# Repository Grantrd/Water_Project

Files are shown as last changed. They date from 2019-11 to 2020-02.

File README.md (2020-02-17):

# Water Quality Monitoring Project
This project for Dr. Gary Mahoney and Dr. Wei Wu, a collaboration between Scott Heggen, Wei Wu and Rodney Grant. It is meant to allow for the measuring and recording of the quality of water in lakes. The project consists of code written in the Arduino ide, using many of its common libraries. It utulizes Eagle Autocad Software for making the schematics and boards, and _________ to mill the PCB's. This is a school project funded by Berea College.

## Specifications
The board we are creating is made for an Arduino Pro Mini, and acts as a shield for it. Therefore the legs of the Pro will need to be soldered going up and have the board sit on top of the Arduino. The board is 1.04 inches across by 1.79 inches long. 

## Required Components
To use this project you will need: 
- An Arduino Pro Mini
- To be able to mill a PCB/ have the milled PCB 
- A 4.7K ohm resistor and a Digital Temperature probe
- An Arduino Micro SD adapter.  
- An analog light sensor
- A real time clock
- 2 1K to 500K Potentiometers
- A set of molex connectors
- A 6 Pin 90 degree Female header terminal.   

## Getting Started
To use the project you need to install the Arduino programming software. Open the code folder of the project, and copy the contents of the arduino libraries folder into the libraries folder of your arduino software, typically located in yourUserName\Documents\Arduino\libraries. Plug in your Arduino Mini Pro and open the Arduino Software. In the software go to "tools" -- "board" -- "Arduino Pro or Pro Mini". Then Go to open and select the Gary_Node_Temp.ino file located in the Arduino Code folder inside the Code folder of the Project. Then Go to "tools" -- "port" and select the port with the arduino connected, you can unplug and replug the arduino to see which port it connects to. Finally verify and upload the code onto the arduino. If the code will not verify, make sure the libraries are located in the correct folder.  

## The Board
Note if you already have the PCB, you can skip the milling section.  

### Milling the Board
...

### Soldering the board 
To solder the board you will need a soldering iron, solder, a milled PCB, and all of the required components listed above. 
You will need to solder the components for the board according to their location on the color coded diagram found under Board Layout. 

For the following components you will need to solder female ended molexes connectors to the board in place of the components, and solder male headed molex connectors to the ends of the components. They will then plug into each other.
- Temperature Probe
- Real Time Clock
- Power Switch
- Light Sensor

For the following components you will need to solder the components themselves to the board directly.
- Power Switch
- 4.7K Resistor
- 2 Potentiometers

For the Micro SD Writer you need to solder a 90 degree 6 pin female header terminal.

### Board Layout
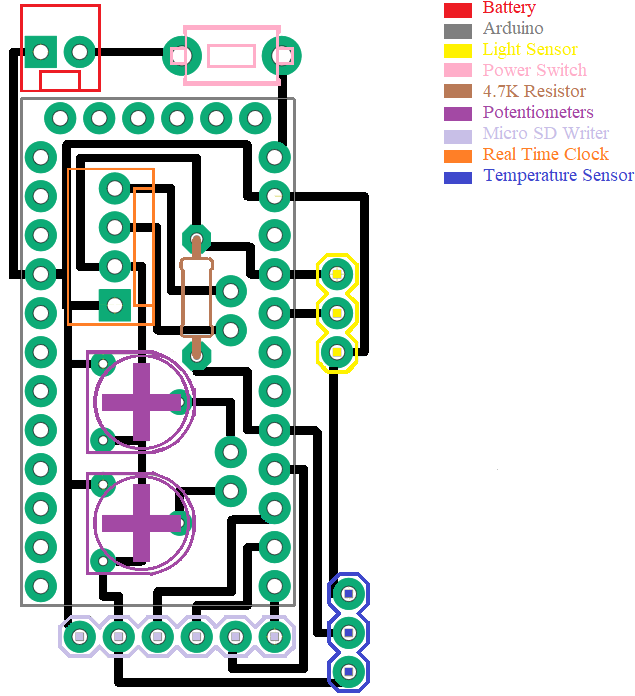
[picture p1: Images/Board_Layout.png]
Board Layout Board


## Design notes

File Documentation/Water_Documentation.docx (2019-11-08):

Water Project Documentation

Parts List/ To Buy

The Arduino we are using, we need 4: https://www.amazon.com/ARCELI-Digispark-Development-Kickstarter-ATTiny167/dp/B07KBFNXMC/ref=sr_1_1?keywords=digispark+pro&qid=1571411723&sr=8-1

The light sensor we need 15:

https://www.adafruit.com/product/1384

The temperature Probe we need one pack of 5:

https://www.amazon.com/Vktech-Waterproof-Digital-Temperature-DS18b20/dp/B00EU70ZL8/ref=sr_1_3?keywords=DS18B20&qid=1571412670&sr=8-3

The Molex connectors:

https://www.amazon.com/Hilitchi-Housing-Connector-Adapter-Perfectly-Compatible/dp/B015Y6JOUG/ref=sr_1_10?keywords=molex&qid=1571412741&sr=8-10

Vertical sliding Switch:

https://www.amazon.com/LIYUDL-Position-Vertical-Switch-SS12D00G3/dp/B075TYP6C5/ref=sr_1_26?hvadid=12092202914&hvbmt=be&hvdev=c&hvqmt=e&keywords=vertical+slide+switch&qid=1572214992&sr=8-26#customerReviews

Schematic/Parts Pinout,

1. Battery connector
2. Temperature probe -pinout: https://external-content.duckduckgo.com/iu/?u=https%3A%2F%2Ftse2.mm.bing.net%2Fth%3Fid%3DOIP.awUXVL5WOeqGfPSrxxb7ewAAAA%26pid%3DApi&f=1
3. Light sensor
4. Real Time clock - DS3231 - pinout: https://components101.com/modules/ds3231-rtc-module-pinout-circuit-datasheet
5. Micro SD Storage Expansion Board Mciro SD TF Card - pinout: https://www.instructables.com/id/Micro-SD-Card-Tutorial/
6. Arduino Tiny - pinout : http://digispark.s3.amazonaws.com/DigisparkProDiagram2.png
7. Power switch - Pinout: https://www.amazon.com/microtivity-IM231-3-pin-Slide-Switch/dp/B008CZIFQG/ref=sr_1_2?keywords=Vertical+Slide+Switch&qid=1572024991&s=electronics&sr=1-2

Board Layout/ Pinout:

1. Temp sensor pinout: PA7 (D5)
2. Light sensor pinout: PA3 (A9)
3. Micro SD pinout: (SC - PB3 (D4), (Mosi - PA4 (Mosi), (Miso - (PA2 (Miso)), (SCK- PA5(SCK)))
4. RT Clock - pinout: ((SDA - PB0 (SDA)), (SCL PB2 (SCL)))

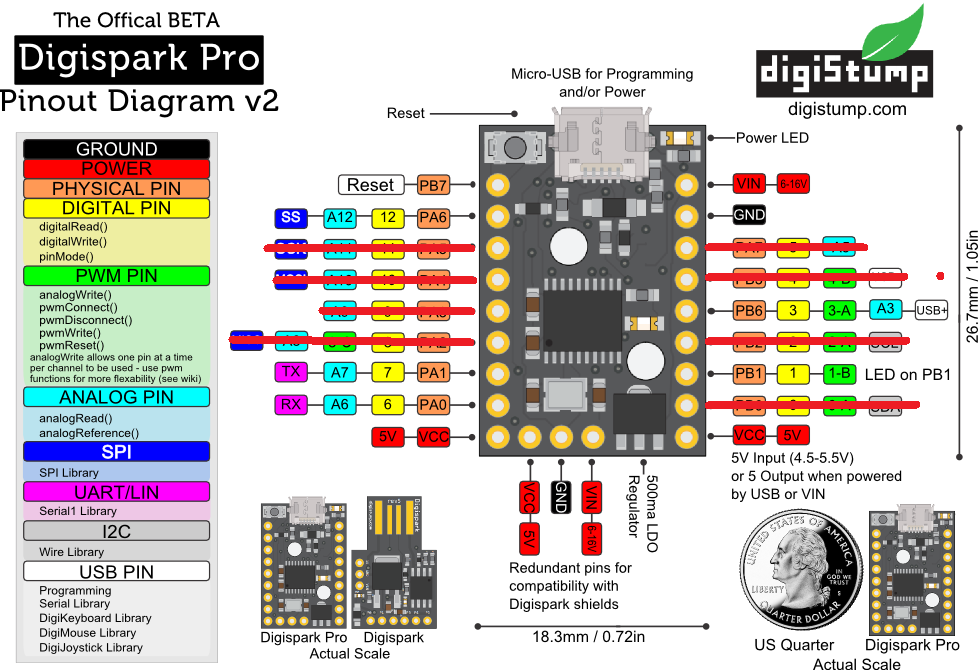
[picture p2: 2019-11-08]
resources/images/DigisparkPInout in progress.png

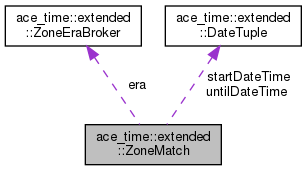
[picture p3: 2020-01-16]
code/Arduino Libraries/AceTime/docs/html/structace__time_1_1extended_1_1ZoneMatch__coll__graph.png

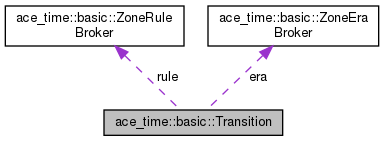
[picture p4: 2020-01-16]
code/Arduino Libraries/AceTime/docs/html/structace__time_1_1basic_1_1Transition__coll__graph.png

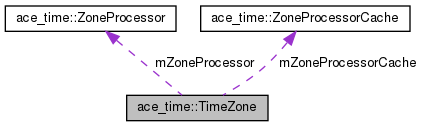
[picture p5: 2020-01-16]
code/Arduino Libraries/AceTime/docs/html/classace__time_1_1TimeZone__coll__graph.png

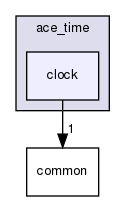
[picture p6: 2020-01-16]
code/Arduino Libraries/AceTime/docs/html/dir_1a3db1509c5a81eeb8e8fbfe5ac0febc_dep.png

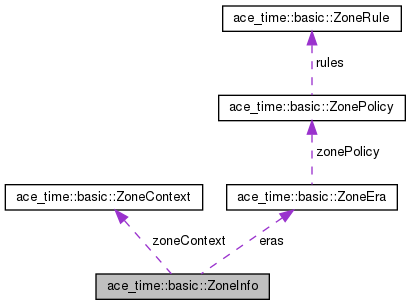
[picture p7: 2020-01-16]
code/Arduino Libraries/AceTime/docs/html/structace__time_1_1basic_1_1ZoneInfo__coll__graph.png

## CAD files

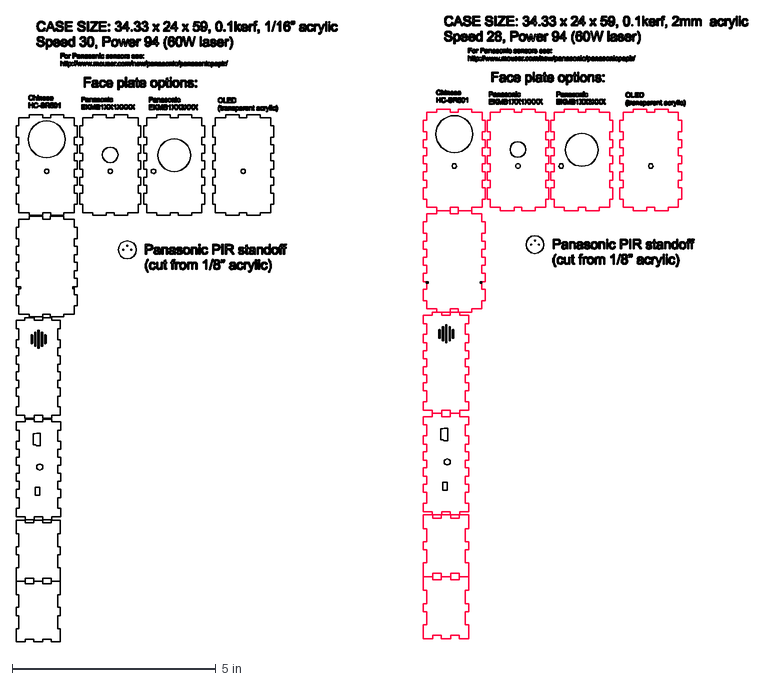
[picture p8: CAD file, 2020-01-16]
code/Arduino Libraries/RFM69_LowPowerLab/Examples/MotionMote/LasercutCase_R3.dxf
18.0 x 15.4 in

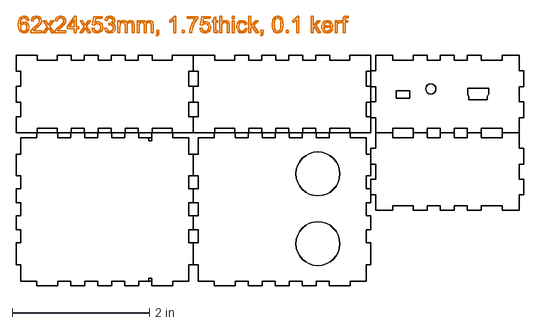
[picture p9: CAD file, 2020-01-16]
code/Arduino Libraries/RFM69_LowPowerLab/Examples/SonarMote/SonarMote_lasercut plans_1.75mm acrylic.dxf
7.41 x 3.94 in

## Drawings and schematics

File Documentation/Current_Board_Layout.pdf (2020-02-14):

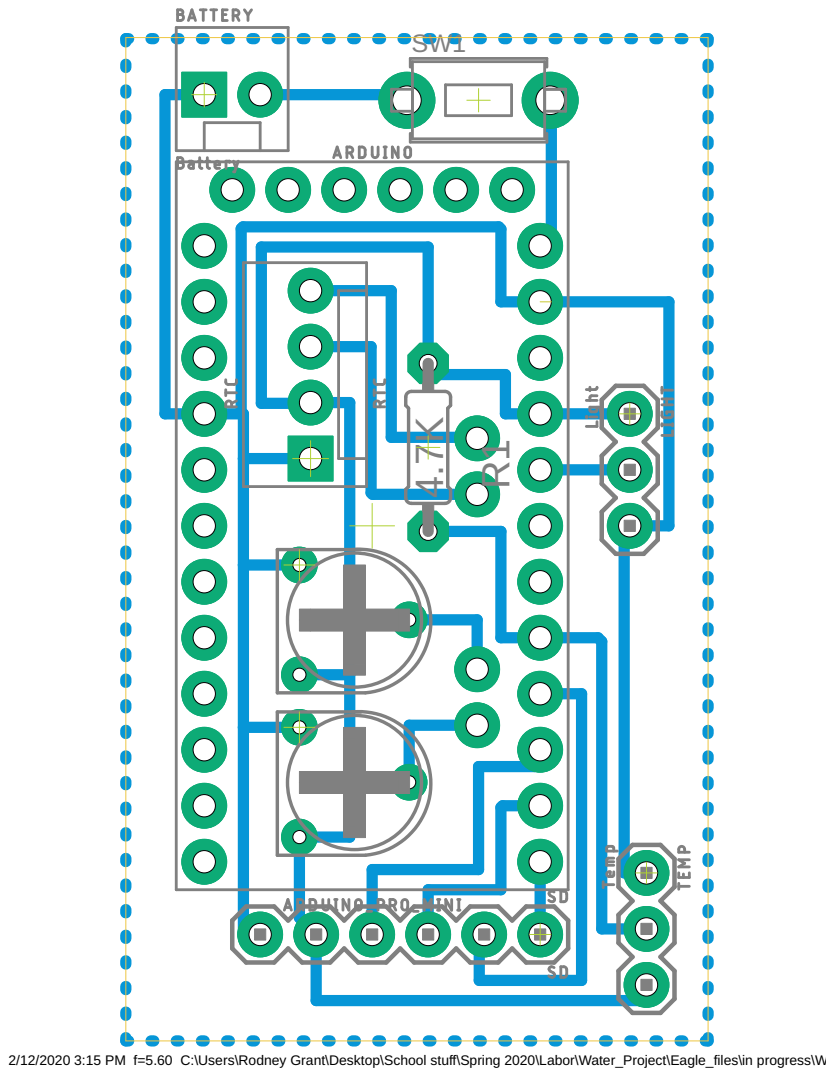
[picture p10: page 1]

2/12/2020 3:15 PM f=5.60 C:\Users\Rodney Grant\Desktop\School stuff\Spring 2020\Labor\Water_Project\Eagle_files\in progress\Water_Schematic2_1.brd

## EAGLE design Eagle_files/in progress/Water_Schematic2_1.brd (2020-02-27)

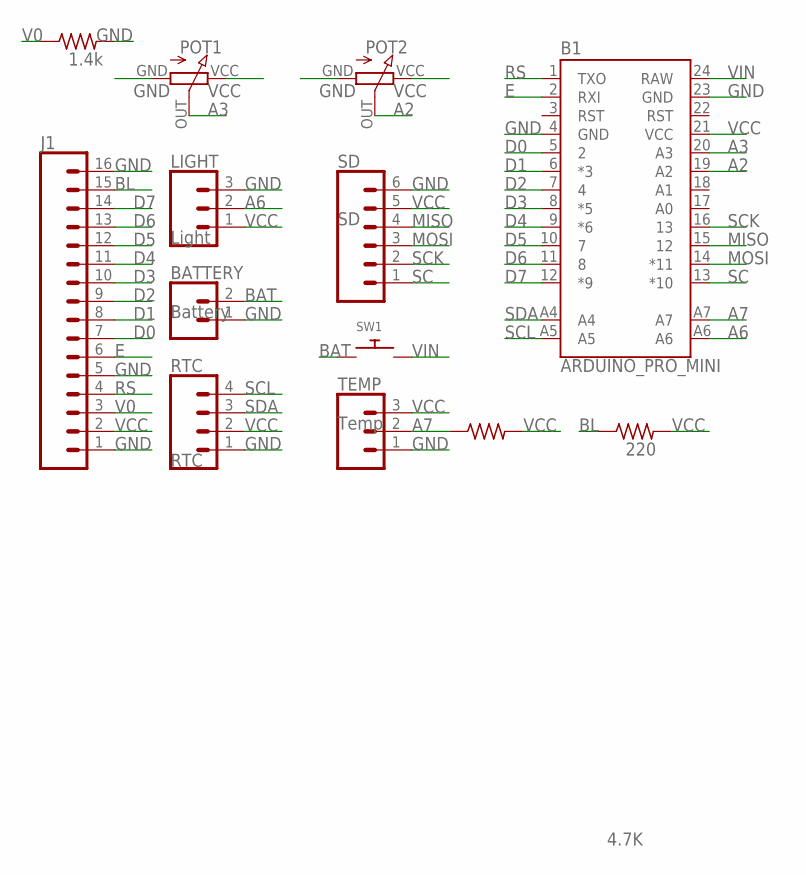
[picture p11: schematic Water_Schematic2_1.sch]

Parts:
B1: ARDUINO_PRO_MINI
BATTERY: Battery; MOLEX-1X2
J1: CONN_16; 1X16
LIGHT: Light; 1X03
POT1, POT2: RM_065
R1: 4.7K; 0204/7
R2: 220; 0204/7
R3: 1.4k; 0204/7
RTC: RTC; MOLEX-1X4
SD: SD; 1X06
SW1: SWITCH_PUSHBUTTONEVQ-PE; TACT_PANA-EVQ
TEMP: Temp; 1X03

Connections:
A2: B1.19 (A2), POT2.OUT
A3: B1.20 (A3), POT1.OUT
A6: B1.A6, LIGHT.2
A7: B1.A7, R1.1, TEMP.2
BAT: BATTERY.2, SW1.P$1
BL: J1.15, R2.1
D0: B1.5 (2), J1.7
D1: B1.6 (*3), J1.8
D2: B1.7 (4), J1.9
D3: B1.8 (*5), J1.10
D4: B1.9 (*6), J1.11
D5: B1.10 (7), J1.12
D6: B1.11 (8), J1.13
D7: B1.12 (*9), J1.14
E: B1.2 (RXI), J1.6
GND: B1.4 (GND), B1.23 (GND), BATTERY.1, J1.1, J1.5, J1.16, LIGHT.3, POT1.GND (GROUND), POT2.GND (GROUND), R3.2, RTC.1, SD.6, TEMP.1
MISO: B1.15 (12), SD.4
MOSI: B1.14 (*11), SD.3
RS: B1.1 (TXO), J1.4
SC: B1.13 (*10), SD.1
SCK: B1.16 (13), SD.2
SCL: B1.A5, RTC.4
SDA: B1.A4, RTC.3
V0: J1.3, R3.1
VCC: B1.21 (VCC), J1.2, LIGHT.1, POT1.VCC, POT2.VCC, R1.2, R2.2, RTC.2, SD.5, TEMP.3
VIN: B1.24 (RAW), SW1.P$2

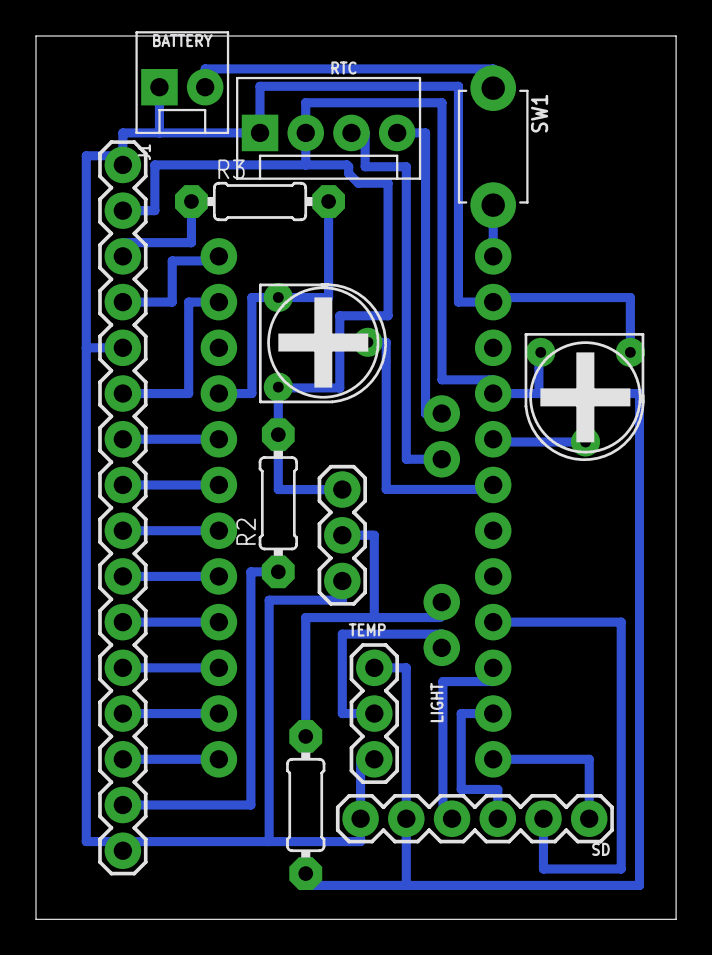
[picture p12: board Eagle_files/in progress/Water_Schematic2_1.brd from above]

Board: 2 copper layers, 35.6 x 49.1 mm, 13 parts (0 on the bottom side), 26 nets.

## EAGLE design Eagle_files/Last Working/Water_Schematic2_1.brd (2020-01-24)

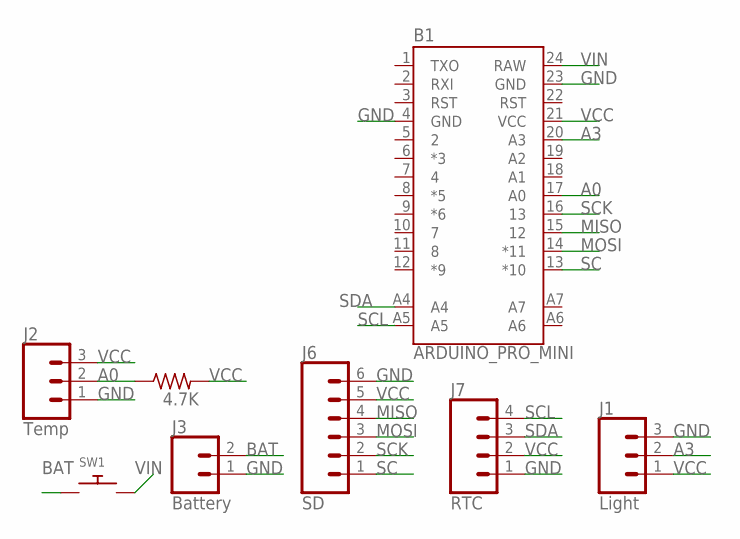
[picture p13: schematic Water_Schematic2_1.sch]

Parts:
B1: ARDUINO_PRO_MINI
J1: Light; 1X03
J2: Temp; 1X03
J3: Battery; MOLEX-1X2
J6: SD; 1X06
J7: RTC; MOLEX-1X4
R1: 4.7K; 0204/7
SW1: SWITCH_PUSHBUTTONEVQ-PE; TACT_PANA-EVQ

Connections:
A0: B1.17 (A0), J2.2, R1.1
A3: B1.20 (A3), J1.2
BAT: J3.2, SW1.P$1
GND: B1.4 (GND), B1.23 (GND), J1.3, J2.1, J3.1, J6.6, J7.1
MISO: B1.15 (12), J6.4
MOSI: B1.14 (*11), J6.3
SC: B1.13 (*10), J6.1
SCK: B1.16 (13), J6.2
SCL: B1.A5, J7.4
SDA: B1.A4, J7.3
VCC: B1.21 (VCC), J1.1, J2.3, J6.5, J7.2, R1.2
VIN: B1.24 (RAW), SW1.P$2

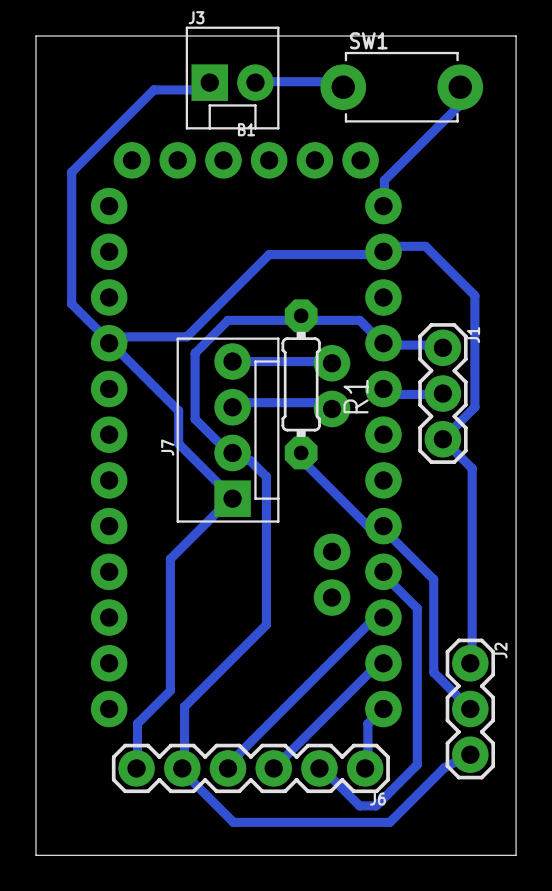
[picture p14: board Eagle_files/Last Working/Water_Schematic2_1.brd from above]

Board: 2 copper layers, 26.7 x 45.5 mm, 8 parts (0 on the bottom side), 12 nets.

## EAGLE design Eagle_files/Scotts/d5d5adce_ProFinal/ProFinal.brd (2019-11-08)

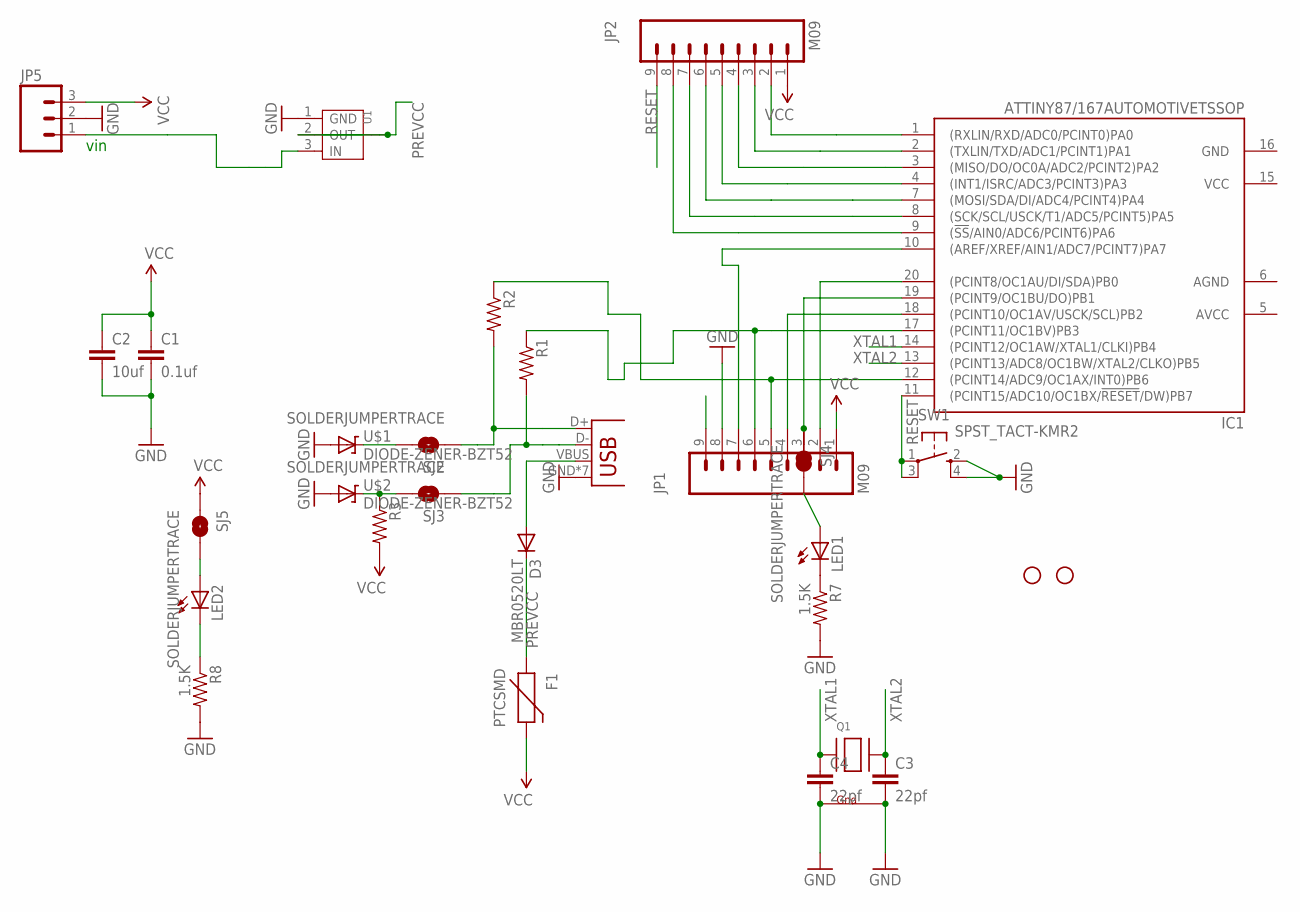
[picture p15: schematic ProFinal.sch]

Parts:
C1: 0.1uf; 0603-CAP
C2: 10uf; 0805
C3, C4: 22pf; 0603-CAP
D3: MBR0520LT; SOD123
F1: PTCSMD; PTC-1206
IC1: ATTINY87/167AUTOMOTIVETSSOP; TSSOP20
JP1, JP2: M09; 1X09
JP5: M03PTH; 1X03
LED1, LED2: LEDCHIP-LED0805; CHIP-LED0805
Q1: XTAL-4-3225; NX3225
R1, R2, R3: RESISTOR0603-RES; 0603-RES
R7, R8: 1.5K; 0603-RES
SJ2, SJ3, SJ4, SJ5: SOLDERJUMPERTRACE; SJ_2S-TRACE
STANDOFF3, STANDOFF4: STAND-OFFTIGHT; STAND-OFF-TIGHT
SW1: SPST_TACT-KMR2; KMR2
U1: LD1117SOT89; SOT89
U$1, U$2: DIODE-ZENER-BZT52; SOD-323
X1: USB-MICROB

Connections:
GND: C1.2, C2.2, C3.2, C4.2, IC1.16 (GND), JP1.8, JP5.2, Q1.2 (G2), Q1.4 (G1), R7.2, R8.2, SW1.2 (S), SW1.4 (S1), U1.1 (GND), U$1.2 (A), U$2.2 (A), X1.GND, X1.P1 (GND), X1.P2 (GND), X1.P3 (GND), X1.P4 (GND), X1.P5 (GND), X1.P6 (GND)
unnamed: IC1.20 ((PCINT8/OC1AU/DI/SDA)PB0), JP1.2
unnamed: IC1.12 ((PCINT14/ADC9/OC1AX/INT0)PB6), JP1.5, R2.1
unnamed: IC1.19 ((PCINT9/OC1BU/DO)PB1), JP1.3, SJ4.1
unnamed: IC1.1 ((RXLIN/RXD/ADC0/PCINT0)PA0), JP2.2
unnamed: IC1.2 ((TXLIN/TXD/ADC1/PCINT1)PA1), JP2.3
unnamed: IC1.3 ((MISO/DO/OC0A/ADC2/PCINT2)PA2), JP2.4
unnamed: IC1.4 ((INT1/ISRC/ADC3/PCINT3)PA3), JP2.5
unnamed: IC1.7 ((MOSI/SDA/DI/ADC4/PCINT4)PA4), JP2.6
unnamed: IC1.18 ((PCINT10/OC1AV/USCK/SCL)PB2), JP1.4
unnamed: R1.2, SJ3.1, X1.D-
unnamed: R2.2, SJ2.1, X1.D+
unnamed: IC1.8 ((SCK/SCL/USCK/T1/ADC5/PCINT5)PA5), JP2.7
unnamed: IC1.9 ((!SS!/AIN0/ADC6/PCINT6)PA6), JP2.8
unnamed: IC1.10 ((AREF/XREF/AIN1/ADC7/PCINT7)PA7), JP1.7
unnamed: IC1.17 ((PCINT11/OC1BV)PB3), JP1.6, R1.1
unnamed: SJ2.2, U$1.1 (C)
unnamed: R3.1, SJ3.2, U$2.1 (C)
unnamed: LED1.C, R7.1
unnamed: LED1.A, SJ4.2
unnamed: LED2.A, SJ5.2
unnamed: LED2.C, R8.1
unnamed: D3.A, X1.VBUS
PREVCC: D3.C, F1.1, U1.2 (OUT), U1.4 (TAB)
RESET: IC1.11 ((PCINT15/ADC10/OC1BX/!RESET!/DW)PB7), JP2.9, SW1.1, SW1.3 (P1)
VCC: C1.1, C2.1, F1.2, IC1.15 (VCC), JP1.1, JP2.1, JP5.3, R3.2, SJ5.1
VIN: JP1.9, JP5.1, U1.3 (IN)
XTAL1: C4.1, IC1.14 ((PCINT12/OC1AW/XTAL1/CLKI)PB4), Q1.1 (X1)
XTAL2: C3.1, IC1.13 ((PCINT13/ADC8/OC1BW/XTAL2/CLKO)PB5), Q1.3 (X2)

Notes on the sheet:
vin

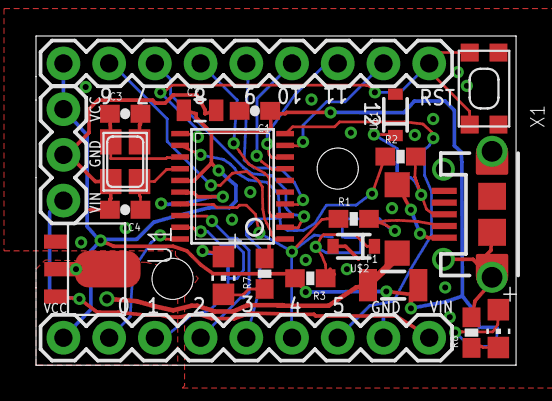
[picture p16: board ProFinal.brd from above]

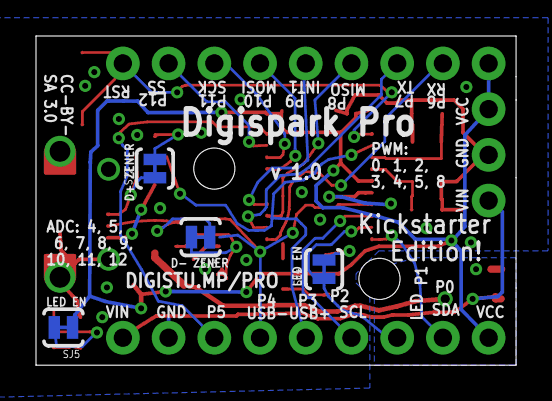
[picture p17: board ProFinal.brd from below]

Board: 2 copper layers, 26.7 x 18.3 mm, 29 parts (4 on the bottom side), 29 nets.

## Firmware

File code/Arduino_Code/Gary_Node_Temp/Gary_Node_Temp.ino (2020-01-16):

#include <OneWire.h>        //Temp (install from library manager)
#include <DallasTemperature.h>  //Temp (install from library manager)
#include <DS3231.h> //RTC  (install from library manager)
#include "SD.h"   //SD card (install from library manager)
#include "LowPower.h" // low power consumption (cpp and h files included)

int Sample_Number=6;   // everytime you sample, take 6 samples.
int minutes_to_wake = 15;  // number of minutes between samples
int wake_counter = 0;
//RTC Setup
DS3231 rtc(SDA, SCL);
//End of RTC setup

//Temp sensor setup
// add a 4.7k Ohm resistor between 5V and data wire
#define TempSensor A0    //Temp
OneWire oneWire(TempSensor);
DallasTemperature sensors(&oneWire);
float Celcius = 0;
float Fahrenheit = 0;

//SD Card setup
const int chipSelect = 10; // for data logging shield
File logfile;
char filename[] = "GaryUW00.txt";
//End of SD Card setup

//Light Sensor Setup
#define LightSensor A3
int Light;
float Lux = 0;
float RawLuxRange = 69666.3 ; // 1024
float LogLuxRange = 500;

#define LEDR 4
#define LEDB 3
//////////////////////////////////////////////////////////////////////////
void setup(void)
{
  pinMode(LEDB,OUTPUT);
  pinMode (LightSensor, INPUT);
  pinMode(chipSelect, OUTPUT);
  //pinMode(LEDR,OUTPUT);
  
  Serial.begin(9600); //Serial port 9600 Baud rate
  rtc.begin(); //RTC begin
//  setDateTime();  // Uncomment to reset the date and time of the RTC
  sensors.begin(); // Temp sensor

//  Serial.println("Starting SD card init");
  while (!SD.begin(chipSelect)) {
//    digitalWrite(LEDR, HIGH);
//    digitalWrite(LEDB, LOW);
    Serial.println("Card failed, or not present");
  }
  Serial.println("SD card initialized.");
  
  //  digitalWrite(LEDR, LOW);
  digitalWrite(LEDB, HIGH);
  delay(800);
  digitalWrite(LEDB,LOW);
 
  //create new log file:
  for (uint8_t i = 0; i < 100; i++) {
    filename[6] = i / 10 + '0';
    filename[7] = i % 10 + '0';
    if (! SD.exists(filename)) {
      // only open a new file if it doesn't exist
      logfile = SD.open(filename, FILE_WRITE);
//      Serial.print("Log file created: ");
//      Serial.print(filename);
//      Serial.println("");
      break;  // leave the loop!
    } else {
//      Serial.print("Log file already exists: ");
//      Serial.print(filename);
//      Serial.println("");
    }
  }
//  Serial.println("Beginning Loop");
}

void loop()
{
 if (wake_counter < minutes_to_wake*60/8) {  // Sleep for: (60s/m * minutes_to_wake)/8s (LowPower max setting)
    wake_counter += 1;
    
//    String ts = generateTimestamp();
//    Serial.println("Sleeping: ");
//    Serial.print(wake_counter);
//    Serial.print(" of ");
//    Serial.print(minutes_to_wake*60/8);
    delay(100);
    LowPower.powerDown(SLEEP_8S, ADC_OFF, BOD_OFF);  //sleep in 8 seconds
  } else {
    wake_counter = 0;
//    Serial.println("Sense time");
    String ts = generateTimestamp();
  
//    Serial.println("Logging to SD");
    logfile = SD.open(filename, FILE_WRITE);
    logfile.print(ts);
      
    for(int j=0;j<Sample_Number;j++){
      sensors.requestTemperatures();
      Celcius = sensors.getTempCByIndex(0);
      Fahrenheit = sensors.toFahrenheit(Celcius);
      Light = analogRead(LightSensor);
      Lux = RawToLux(Light);
      
      logfile.print(" Temp  ");
      logfile.print(Fahrenheit);
      logfile.print(" F  ");
      logfile.print(" Lux ");
      logfile.println(Lux);
      
//      Serial.print(" Temp: ");
//      Serial.print(Fahrenheit);
//      Serial.print(" F; ");
//      Serial.print("Lux: ");
//      Serial.println(Lux);
      delay(100);
    }
    logfile.close();
//    Serial.println("log file closed");
  
      
    
//    Serial.println("Going to sleep");
    delay(100);
    // Sleep for 8 s with ADC module and BOD module off
    LowPower.powerDown(SLEEP_8S, ADC_OFF, BOD_OFF);  //sleep in 8 seconds
  }
}

float RawToLux(int raw)
{
  float logLux = raw * LogLuxRange / RawLuxRange; // rescale
  return pow(10, logLux); // log function 
}

void setDateTime() {
  rtc.setDOW(WEDNESDAY);     // Set Day-of-Week 
  rtc.setTime(22, 14, 0);     // Set the time 
  rtc.setDate(11, 12, 2019);   // Set the date (day, month, year)
}

String generateTimestamp() {
  String s = rtc.getDOWStr();
  s += " ";
  s += rtc.getDateStr();
  s += " -- ";
  s += rtc.getTimeStr();
  s += ":";
//  Serial.print("The time is: ");
//  Serial.print(s);
  return s;
}

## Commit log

2019-11-08 initializing repo
    [ProFinal.brd, ProFinal.sch, Water_Schematic2_1.brd, Water_Schematic2_1.sch]
2019-11-14 cam output for mill
    [copper_bottom.gbr, drill_1_16.xln, profile.gbr]
2019-11-22 up to date
    [a06_username_copper_Water_Schematic2_1_Copper.gbr, a06_username_dim_Water_Schematic2_1_Dimension.gbr, a06_username_drills_Water_Schematic2_1_Drills.xln]
2019-12-12 New Arduino code that works with Scott's protoboard
2019-12-12 Moving files around to make things more clear
    [ProFinal.brd, ProFinal.sch, Water_Schematic2_1.brd, Water_Schematic2_1.sch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]
2019-12-12 Eagle files updated
    [Water_Schematic2_1.brd, Water_Schematic2_1.sch]
2019-12-13 Updated code to remove any extra processing, such as Serial prints; Wakes up for sensing every 15m now also
2019-12-13 Minor tweaks to the board layout
    [Water_Schematic2_1.brd]
2020-01-16 Added Arduino libraries needed for the code to work.
    [LasercutCase_R3.dxf, SonarMote_lasercut plans_1.75mm acrylic.dxf]
2020-01-24 added a more spaced out brd
    [ProFinal.brd, ProFinal.sch, Water_Schematic2_1.brd, Water_Schematic2_1.sch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]
2020-01-27 Updating board
    [Water_Schematic2_1.brd]
2020-02-10 Updated design
    [LasercutCase_R3.dxf, ProFinal.brd, ProFinal.sch, SonarMote_lasercut plans_1.75mm acrylic.dxf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]
2020-02-14 updating readme
    [Water_Schematic2_1.brd]
2020-02-18 Removing unnecessary files; minor tweaks to board and schematic, like removing value from pots
    [Water_Schematic2_1.brd, Water_Schematic2_1.sch]
2020-02-24 almost there brd
    [Water_Schematic2_1.brd, Water_Schematic2_1.sch]
2020-02-25 almost there!!!!!!
    [Water_Schematic2_1.brd, Water_Schematic2_1.sch]
2020-02-25 got the latest schematic working
    [Water_Schematic2_1.brd, Water_Schematic2_1.sch]
2020-02-26 attempt 2 lcd
    [Water_Schematic2_1.brd, Water_Schematic2_1.sch]
2020-02-27 Removing unnecessary files, again. Made very minor change to board:
    [Water_Schematic2_1.brd]

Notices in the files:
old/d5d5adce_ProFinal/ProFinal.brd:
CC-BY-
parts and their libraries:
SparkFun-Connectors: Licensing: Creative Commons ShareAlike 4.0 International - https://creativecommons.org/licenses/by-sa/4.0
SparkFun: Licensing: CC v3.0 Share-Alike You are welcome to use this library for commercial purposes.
